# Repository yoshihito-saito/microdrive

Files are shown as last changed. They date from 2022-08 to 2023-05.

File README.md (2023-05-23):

# Microdrive for multi-site tetrode recording


## Description
* Microdrive for 16 tetrodes.
* This microdrive consists of the following parts.
  * Drive body
  * Shuttle
  * Guide
* You can record from any region by re-design the guide part.
  * [Guide part design tutorial](https://gist.github.com/yoshihito-saito/2603be5581b5dd010331ef912d4f67f2)
 ## Parts list
  * Drive body: 3D print
  * Shuttle: 3D print
  * Guide: 3D print
  * Drive holder: 3D print
  * Drive screws: OpenEphys
  * Shuttle tube: FLXBLE FUSED TUBING TSP100170 PRC PER MR (Mouser Electronics)
  * Guide tube: PIT-FS 0.20 x 0.02 (Furukawa)
  * 64ch EIB (Open Ephys)
  * Gold pin small (Neuralynx)
  * Gold pin large (Neuralynx)

## 3D printer
* FLASHFORGE Foto8.9s: XY axis resolution, 0.05 mm

## Reference electrode making
    1. Cut a coated lead wire into 2 cm lengths (x2).
    2. Strip the wire coating from both ends (~2 mm).
    3. Melt solder and apply to both ends.
    4. Hold a M0.8x2 screw in a vice.
    5. Apply a small amount of flux to the screw.
    6. Solder one end to the screw.
    7. Solder another end to a connector (Preci-Dip, 851-83-050-10-001101) (Reference electrode).
    8. Solder one end of the remaining wire to the pin connector (Reference wire).

## Microdrive construction

#### 1. Guide part construction.
    1. Cut guide tubes into 2 cm long.
    2. Bundle the guide tubes into holes of the guide part.
    3. Cut both sides of the guide tubes to adjust the height.
    4. Move down the guide tubes so they don't pop out into the drive inside.
    5. Cut the guide tubes about 5 mm from the drive bottom.
    6. Fix the guide tubes to the guide part by adhesive.
    7. Cut the guide tubes to match the height to the brain surface of your coordination.
    8. Apply a small amount of adhesive to bind the guide tubes.
    
#### 2. Drive body construction.
    1. Put a shuttle on a lane of the drive body and fix the shuttle to a drive screw (x16).
    2. Check the shuttle motion by rotating the screw.
    3. Fix the drive screws into the pocket on the top of the drive body with a light curing resin.


#### 3. Shuttle tube insertion
    1. Fix the guide part to the drive body by adhesive.
    2. Cut shuttle tubes into 3 cm long.
    3. Apply silicon oil on the surface of shuttle tubes as lubricant.
    4. Insert shuttle tubes into the guide tubes and hook into the shuttles.
    5. Adjust the position of shuttle tube so that the depth is about 1 mm from the top of the guide tube.
    6. Fix the shuttle tube to the shuttle by adhesive.
    7. Cut the top end of the shuttle tubes.
    
#### 4. Electrode loading.
    1. Fix the microdrive to the drive holder.
    2. Load a tetrode into a shuttle tube (x16).
    3. Connect the tetrode to the EIB with small gold pin.
    4. Fix the tetrode to the shuttle tube by adhesive.
    5. Cut the end of the tetrodes and align the height of it to the bottom end of the guide tube array.
    6. Rotate the EIB.
    7. Connect the reference wire to the reference channel and GND channel of the EIB with large gold pin or soldering.
    8. Lower the EIB to the top of the microdrive.
    7. Fix the EIB to the microdrive by adhesive.  
    8. Paint the drive body with a conductive paint and electrically connect with the GND.




#### 5. DiI coating and Mineral oil filling
    1. Lower all tetrodes and apply DiI solution (1 mg/mL in 100% EtOH) to the tetrode ends.
    2. Withdraw all tetrodes to the lower end of the guide arrays.
    3. Dip the guide arrays into mineral oil (Sigma) and fill the inside of the guide arrays.
     * Caution: This procedure prevents blood from flowing back into the guide arrays. If this is not done well, the tetrodes will get stuck.

## Surgical procedure
#### Materials
- Mouse
- Microdrive
- Ref electrode
- Dental drill
  - For skrew implant: Ela steel bur Raund 1/2 
  - For craniotomy: Miniature Carbides Ball Shape Burs (A-212-02)
- Silicone oil (Sigma, 378429)
- Dental Cement

#### Procedure (Protrocols must be approved by your institution.)
     1. Mark the bregma and lambda.
     2. Align bregma and lambda horizontally.
     3. Mark on your coordinates.
     4. Mark on cerebellum for the reference electrode. → Drill the hole by 1/2 drill.
      * Caution. You should check the location of the blood vessels before marking. Applying saline will help you see the location.
     5. Perform craniotomy and duratomy.
      * Caution. To stop bleeding and keep the brain surface moist, use collagen sponges and saline or ACSF.
     6. Measure the difference of the height of the brain surface of each target region.
     7. Move all tetrode positions to match the height of each brain surface.
     8. Place reference electode screw on cerebellum.
     9. Lower the microdrive and attach the tetrode ends to the brain surface and fill the cranial window around the guide arrays with silicone oil.
     10. Fix the microdrive with dental cement.
     21. Recover
     22. Lower one tetrodes per region into the brain each hour (~300 μm).
      * Caution. Do not lower all the tetrodes at the same time as this will increase the surface area, spread the pressure and make it more difficult to penetrate the brain surface.

## License
The design of this microdrive was inspired by "[Shuttledrive](https://github.com/open-ephys/shuttle-drive)" by Jakob Voigts and Jonathan P. Newman.

The designs are licensed under a [Creative Commons Attribution-NonCommercial-ShareAlike 3.0 IGO License](https://creativecommons.org/licenses/by-nc-sa/3.0/igo/)(CC BY-NC-SA).

Copyright Yoshihito Saito 2023.

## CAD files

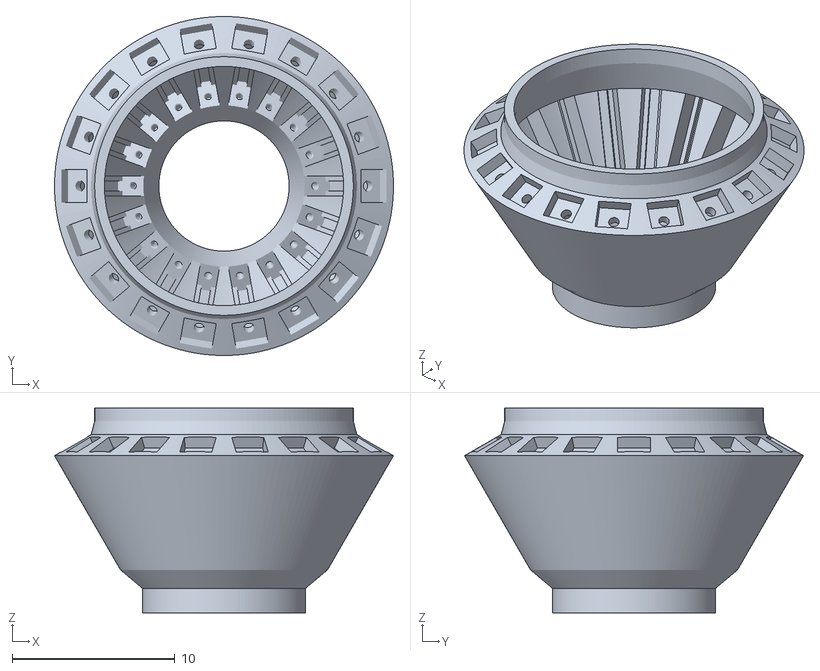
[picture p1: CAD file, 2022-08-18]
stl/Drive_body.stl
20.8 x 20.8 x 12.6

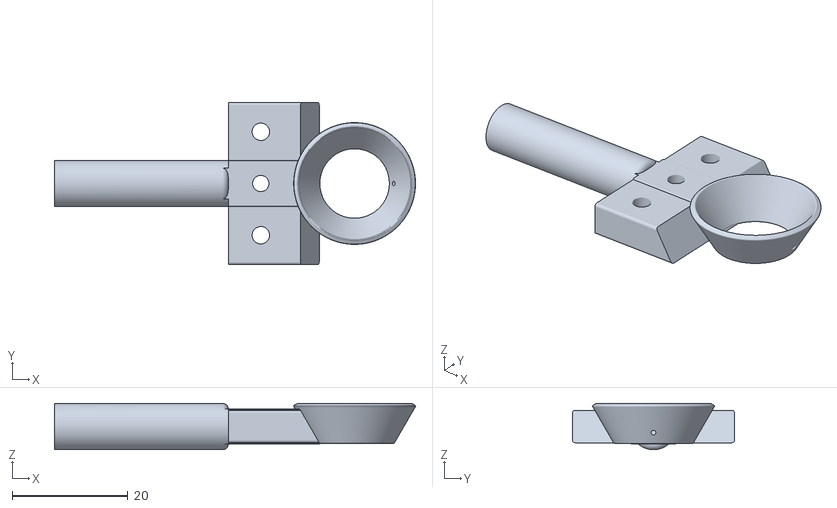
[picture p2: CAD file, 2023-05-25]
stl_for_Foto8.9s/Microdrive_holder.stl
62.3 x 28.0 x 8.01

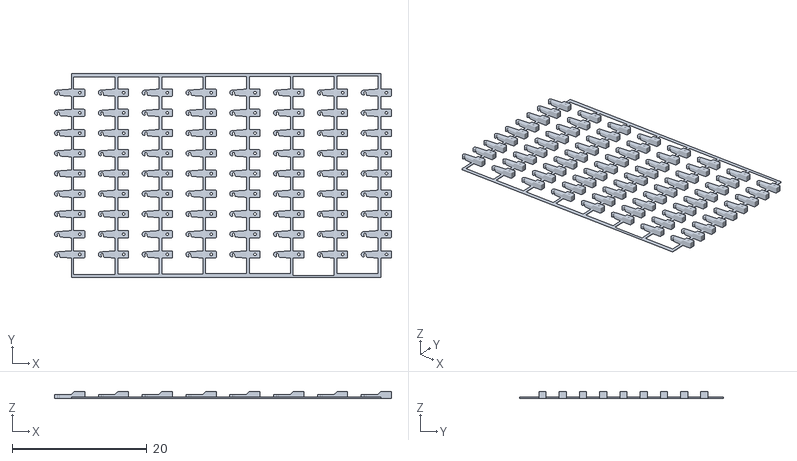
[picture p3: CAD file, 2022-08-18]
stl/shuttle.stl
50.0 x 30.2 x 1.00

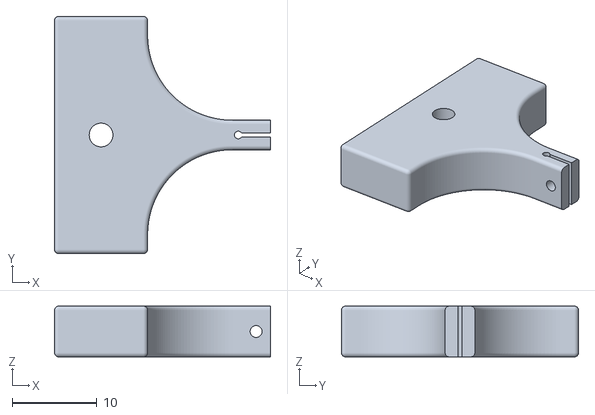
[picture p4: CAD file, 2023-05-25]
stl_for_Foto8.9s/EIB_holder.stl
25.5 x 28.0 x 6.00

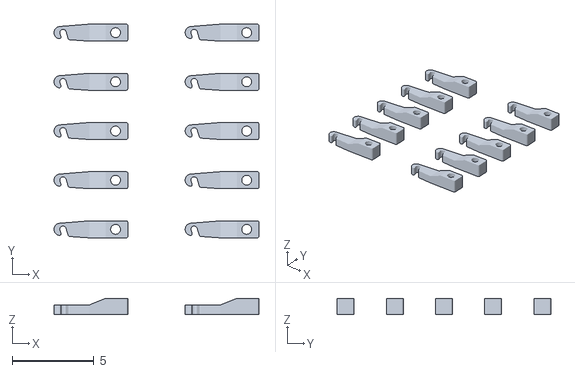
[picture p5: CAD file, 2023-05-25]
stl_for_Foto8.9s/Shuttle_Foto8.9s_ver9.stl
12.5 x 13.0 x 1.00

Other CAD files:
stl_for_Foto8.9s/Body_Foto8.9s_ver5.stl
